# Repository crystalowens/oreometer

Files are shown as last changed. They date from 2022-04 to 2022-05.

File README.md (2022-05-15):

# How to print and use the Oreometer

When you want to study the fluid mechanics of food, or "**Fooid Mechanics**," with scientific rigor, you need a tool to make quantitative measurements. Here, we share printable files so that anyone with access to a 3D printer can make their own Oreometer, for measuring the rheology of Oreos and other sandwich cookies and snacks. 

This work is associated with a [publication in the Physics of Fluids](https://aip.scitation.org/doi/full/10.1063/5.0085362), which has more detail on the physics and rheology of Oreo creme as measured on our laboratory rheometer and on our original Oreometer. 

>On Oreology, the fracture and flow of “milk’s favorite cookie®” 
>by Crystal E. Owens (crystalo@mit.edu), Max R. Fan (范瑞), A. John Hart, and Gareth H. McKinley

Sections in this ReadMe: 

[1. 3D printing instructions](#3d-printing-instructions)

[2. Guided tutorial on using the Oreometer](#guided-tutorial-on-using-the-oreometer)

## 3D printing instructions

Design file set: Complete files are included [in this current github repo](https://github.com/crystalowens/oreometer/tree/main/printable-files) to print a full Oreometer including .stl file format to be directly printable after slicing and .step file format to allow easy import and manipulation in most CAD software. If you want to modify the files, we recommend Autodesk Fusion 360, which is available with a free license for educational use. If you come up with a cool modification, please share with us! 

Designs were made in Fusion 360 and printed out of PLA using a Creality Ender 3. Parts were sliced with Cura using a 0.3mm layer height, 20% infill, 210°C extruder temperature, and 55°C bed temperature, and printed with supports for the base halves, Oreo clamps, and penny castles. If a 3D printer isn’t available, parts could be printed at a local makerspace, in a local school or library that has a 3D printer, or ordered from a 3D printing service bureau. 3D printed plastic is often not "food-grade", so Oreos used for rheology experiments should not be consumed if this is the case for your printed parts! 

<p align="center">
 
</p>

This is an example layout in Cura to print one large penny castle and Oreo base half. The gray box around the penny tower is a support blocker that prevents supports from being generated in all the windows (for ease of removal). But it's not necessary for printing quality. 

<p align="center">

</p>

The fully-printed design has a two-part front clamp, two-part back clamp, two penny castles, a two-part base, a bolt, and a nut, assembled as shown. Additional items are rubber bands (we used Advantage Rubber Bands #64 with dimensions 3 1/2 x 1/4 in) and pennies (~2.5 g each) or dimes (~1 g each) to fill one of the penny castles. 

<p align="center">

</p>

All printed and required parts are shown here, with one Oreo clamp assembled around a cookie. 

<p align="center">

</p>

Fully-printed and assembled Oreometer, ready for use! 

**Animated Oreometer assembly video**: https://youtu.be/V_gaJ4po_Nw

## Guided tutorial on using the Oreometer

This section walks you through steps to use the Oreometer, with questions and activities to guide investigation.  

**Learning objectives**

•	Be able to define rheology and what it is used for 

•	Understand and be able to measure failure stress for soft solids

•	Be able to explain why torque may be different for different cookies but material stress is the same 

•	Be able to define adhesive and cohesive failure and explain the difference

•	Be able to make your own measurements at home and understand the results

**Background**

Torque is a measure of how much “twist” you apply around a point. Shear stress is the stress in the material in response to this torque and can be calculated by considering the different geometric factors. For example, a disk with small radius and a disk with large radius, made from the same material, will deform with the same shear stress, but the torque will be much greater for the larger disk. Specific equations to convert between torque and stress are included in our paper. 

Rheology is the study of this material deformation for soft solids including creams, cheeses, and more, and a rheometer is the machine we use in a laboratory to measure this property, which is characterized as viscosity (for simple fluids) or rheology (for complex or non-Newtonian fluids that have a non-constant viscosity). 

Oreos consist of two wafers with creme sandwiched in between. The creme-wafer interface is an adhesive contact since it is between two different materials. It is not a chemical bond, but a physical interface. The interfaces within the creme are cohesive since they are physical contact within the same material. If the Oreo breaks between the creme and wafer (a clean break), this is adhesive failure, whereas if the Oreo breaks so that creme is on both wafers, this is cohesive failure.

**Introduction**

“Frugal science” is a method of making high-tech but low-cost equipment for scientific measurements outside of research labs. Rheometers and other lab equipment are typically very expensive, over USD$100,000, but our 3D printed Oreo twister (which we will call the “Oreometer”) provides a simple, cheap way to study the same basic fluid properties. 

**Materials**

1. One box of Oreos (any type), sandwich cookie, or fluid between disks that is approximately Oreo-sized
2. 100 Pennies
3. 2 rubber bands
4. Printed parts from CAD files
5. Optional: milk

**Procedure:**
1.	Load Oreo into clamps using the suggested rubber band configuration or a configuration of your choosing. Keep in mind that there are two types of clamp halves: front clamp and back clamp. A front clamp has a slot on the side for a penny castle whereas a back clamp does not. Be sure to place clamps of the same type together. 

* _What do different rubber band patterns on the clamps do? Can you make one that is too tight? Too loose?_

2.	Load the clamped Oreo onto the two base halves (which are identical) and adjust the spacing using the nut and bolt. Twist the bolt clockwise until the base halves are close enough to keep the clamps from falling out, but not so close that they squeeze the clamps.

* _Why shouldn’t the base halves be moved so close together that they squeeze the clamps?_

3.	Place the two penny castles into the slots located on the sides of the front clamp. 

* _Why are there two penny castles? Can you use just one?_

4.	Start inserting pennies into one of the penny castles until the Oreo twists apart. For easy counting, the windows on the outside of the penny castle are each 5 pennies tall. Below the center of the front clamp, there are tick marks to indicate whether the Oreo has begun to twist. The tick marks are spaced 9° apart, or 1/40th of a revolution.

* _Before creme failure, how much does the Oreo rotate, if at all? After failure, is the creme split evenly onto both wafers or does one wafer have more creme than the other?_

5.	Record the number of pennies required to cause the Oreo to twist apart. Unclamp the broken Oreo and test out several more Oreos.

* _What was the maximum and minimum number of pennies required to twist an Oreo? What was the average number of pennies? Given that the mass of a penny is 2.5 grams and the arm length of the Oreometer is 90 mm, what torque and stress does this correspond to?_

* Extra 1: See if you can get the Oreo to twist by letting pennies sit in the penny castle for an extended time. Even with low stresses, Oreos will continue to deform slightly, which is called [creep](https://en.wikipedia.org/wiki/Creep_(deformation)), and sometimes they will suddenly fail, even though no more stress has been applied. This phenomenon is known as delayed yielding, and is related to how landslides and avalanches happen. (Snow and mud are yield stress fluids!) Record the number of pennies and time it took for the Oreo to twist. What is the least number of pennies you can use and still see it yield?  

* Extra 2: Test out stale, heated, or frozen Oreos. What effect does this have on the number or pennies required to twist the Oreos? How is the creme distributed on the Oreos affected? What temperature gives the cleanest wafer/creme surface? 

* Extra 3: Test out different Oreo variations such as mint or Double Stuf or even other cookies of similar shape. How many pennies are required now? Is the creme distribution affected?

* Extra 4 (design skills required!): Design and print your own cookie "wafers" as two disks that are 46 mm in diameter and about 2 mm in thickness. For best results, add some texture to one surface. Alternatively, find other cookies or crackers of similar size. Use these to make your own sandwiches with other complex fluids in between. How does the yield stress of peanut butter compare to Oreo creme? Hot sauce? Can you find a stronger fluid in your kitchen?   

* What other questions do you have? 

<details>
 <summary><b>Some observation and results (click to reveal) </b></summary>

 In our lab, we found that normal Oreos take around 30-60 pennies to break. However, Oreos that have been heated, chilled, or become stale will likely require more or fewer pennies. 
 
 It is common to see clean breaks (adhesive failure profiles). This is likely due to [the way Oreo-like cookies are manufactured](https://www.youtube.com/watch?t=193&v=HlZmDxcbpWw&feature=youtu.be), where the creme seems to bond more weakly with one of the wafers. Oftentimes, within an Oreo box most of the weak wafer-creme bonds will be on the same side for all the Oreos, and also affected by the location of the Oreos inside the box. 
 
 The record in our lab for the fewest pennies to break an Oreo open was 10. We left our Oreometer set up overnight, and it was twisted open by the next morning (due to delayed yielding). Can you make it happen with fewer? 
 
  Find more details of our observations in [our full paper in the Physics of Fluids](https://aip.scitation.org/doi/full/10.1063/5.0085362)
 
 </details>

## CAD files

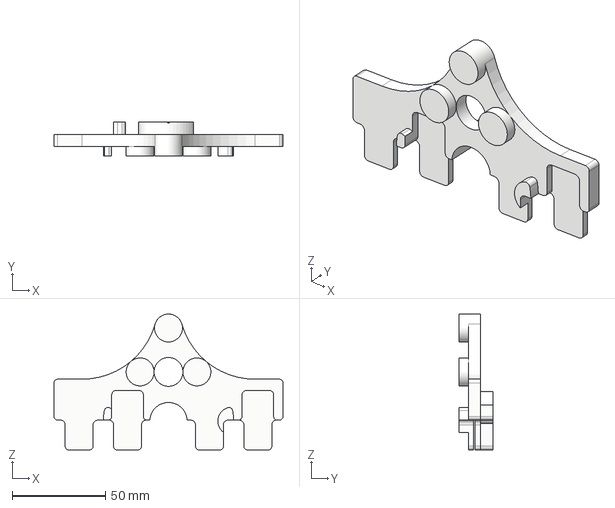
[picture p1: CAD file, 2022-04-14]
printable-files/STEP Files/Clamp - Back.step
123.0 x 18.0 x 73.0 mm

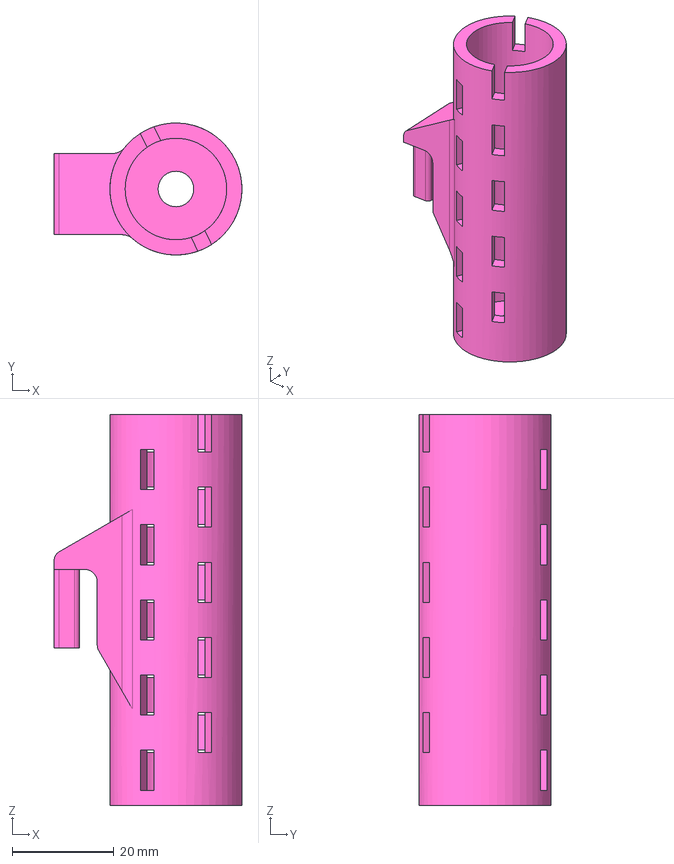
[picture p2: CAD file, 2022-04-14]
printable-files/STEP Files/Penny Castle.step
37.0 x 26.0 x 77.0 mm

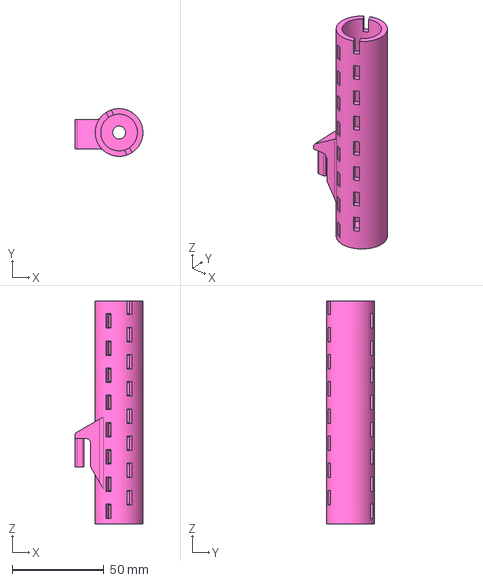
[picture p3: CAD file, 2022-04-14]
printable-files/STEP Files/Penny Castle - Large.step
37.0 x 26.0 x 121.4 mm

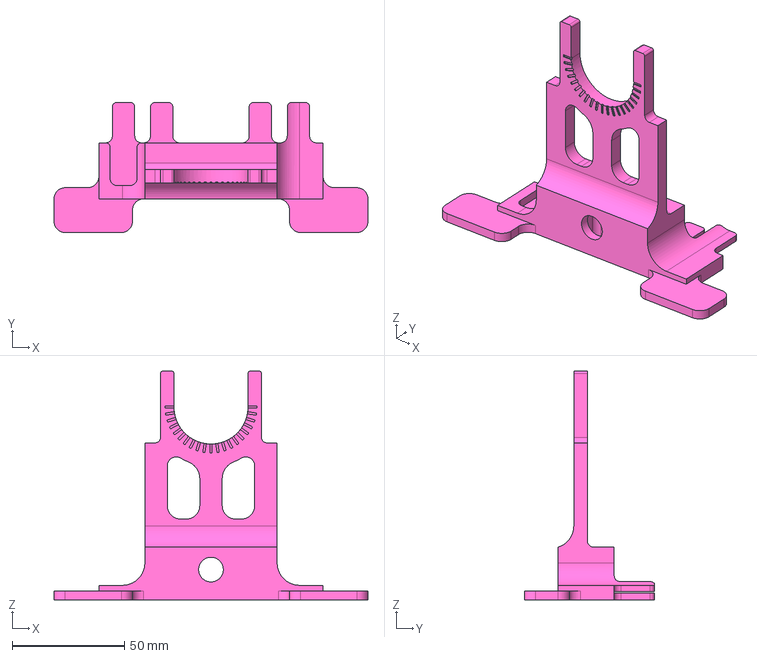
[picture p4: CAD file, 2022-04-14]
printable-files/STEP Files/Base Half.step
140.0 x 58.0 x 102.0 mm

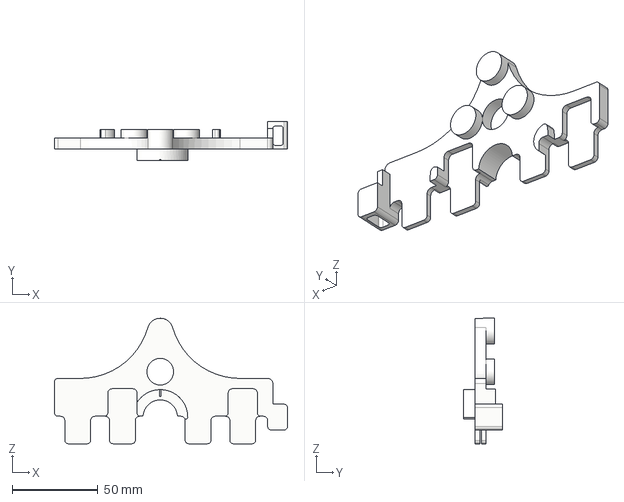
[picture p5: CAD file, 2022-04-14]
printable-files/STEP Files/Clamp - Front.step
135.5 x 22.5 x 73.0 mm

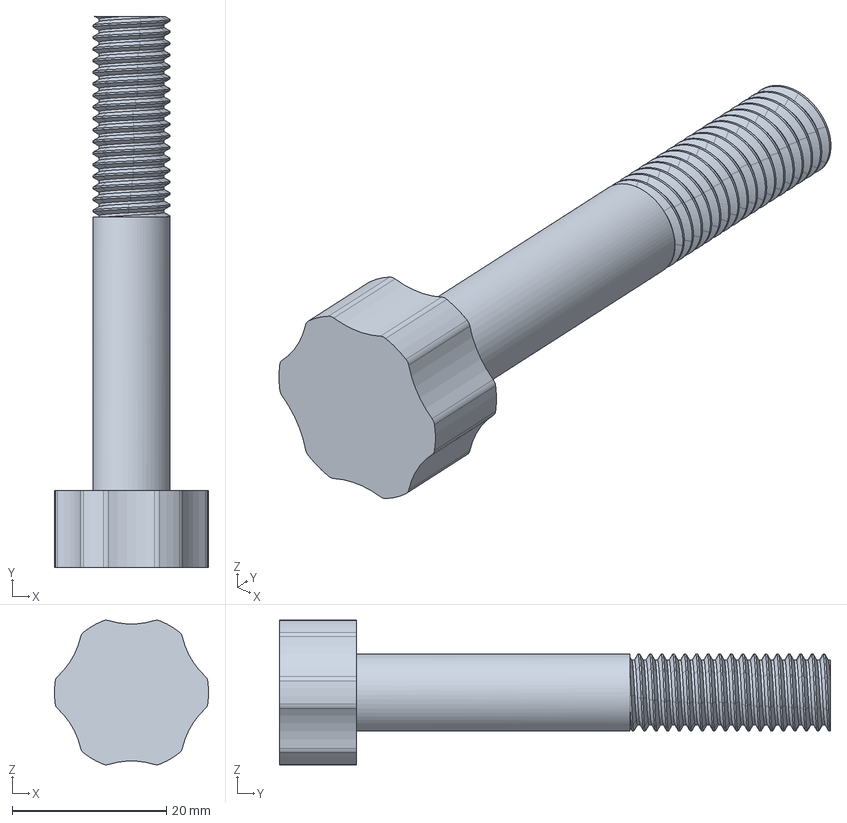
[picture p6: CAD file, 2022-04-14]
printable-files/STEP Files/Bolt.step
20.0 x 71.5 x 18.8 mm

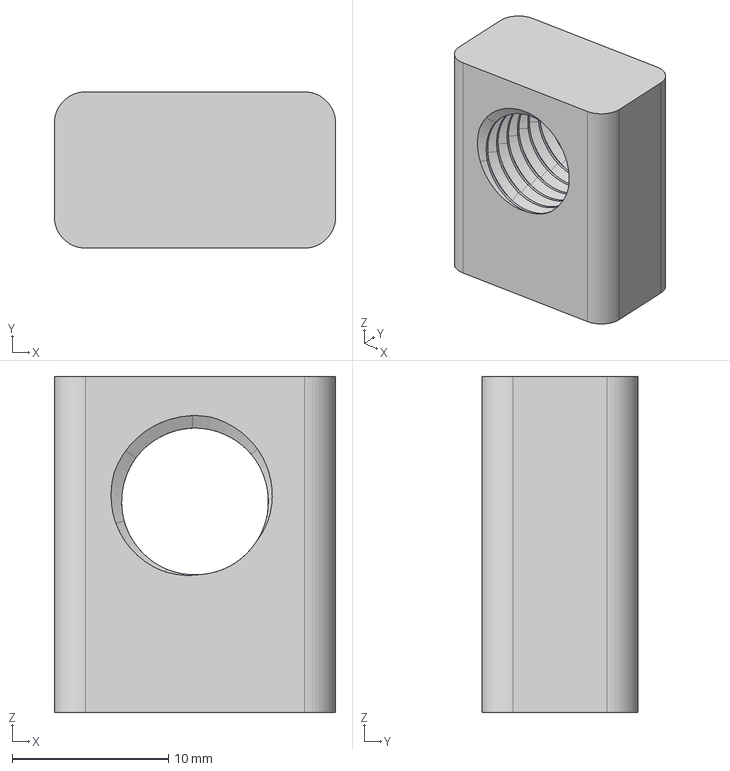
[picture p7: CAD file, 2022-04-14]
printable-files/STEP Files/Nut.step
18.0 x 10.0 x 21.5 mm

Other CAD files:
printable-files/STL Files/Base Half.stl
printable-files/STL Files/Bolt.stl
printable-files/STL Files/Clamp - Back.stl
printable-files/STL Files/Clamp - Front.stl
printable-files/STL Files/Nut.stl
printable-files/STL Files/Penny Castle - Large.stl
printable-files/STL Files/Penny Castle.stl
